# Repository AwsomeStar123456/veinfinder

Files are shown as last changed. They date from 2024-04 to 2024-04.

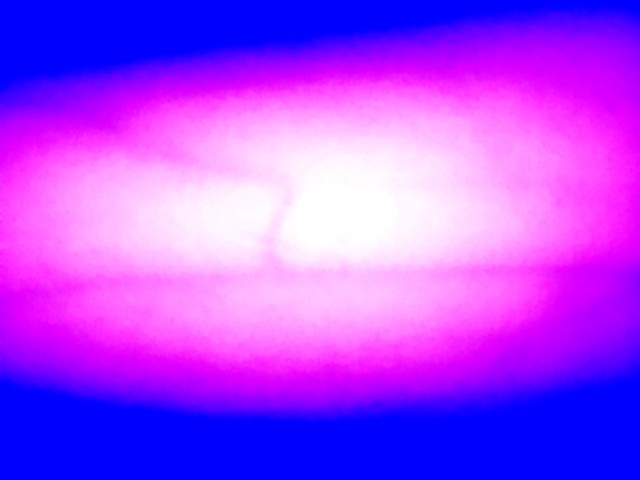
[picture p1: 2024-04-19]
Images/Original Image Set - Copy/Input/62.jpg

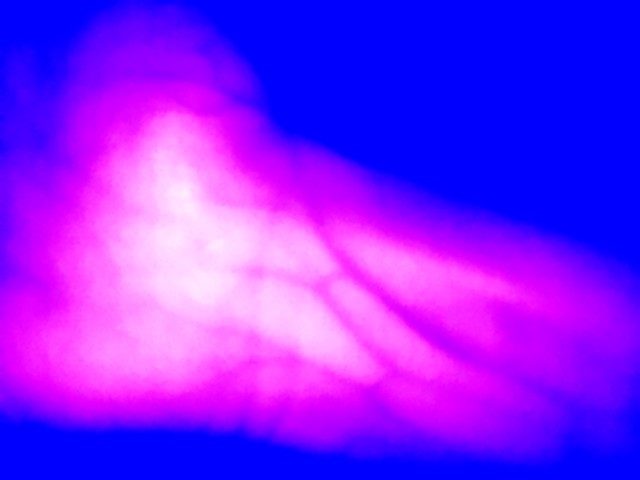
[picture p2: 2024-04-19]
Images/Original Image Set - Copy/Input/38.jpg

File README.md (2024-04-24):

# Veinfinder Project
This is the GitHub for the veinfinder project. Our project uses an IR emitter array with a NoIR Picam which has a IR pass filter on it. Using this we can see veins on peoples arms.

## Team Members
Donggi Lee | u1376432 | donggi2834@gmail.com <br />
Semrah Odobasic | u1293090 | semrahodobasic@icloud.com <br />
Logan Allen | u1190764 | Logan.Allen@utah.edu <br />
Jin Jeong   | u1375534 | djwls97865@gmail.com <br />

## Parts List
Raspberri Pi 2: https://www.raspberrypi.com/products/raspberry-pi-2-model-b/ <br />
NoIR PiCam 2: https://www.raspberrypi.com/products/pi-noir-camera-v2/ <br />
IR Emitter Array: https://www.ebay.com/itm/203067233072?chn=ps&norover=1&mkevt=1&mkrid=711-117182-37290-0&mkcid=2&mkscid=101&itemid=203067233072&targetid=2295557531990&device=c&mktype=pla&googleloc=9029771&poi=&campaignid=19851828444&mkgroupid=160536780385&rlsatarget=pla-2295557531990&abcId=9307249&merchantid=101644847&gad_source=1&gclid=Cj0KCQjwiYOxBhC5ARIsAIvdH51PvhkMOsm8p80wdNCZ_c5YhiLxNzNg80BskEwZZuzRu6qdxxyuCBwaApDhEALw_wcB <br />
Projector: https://www.amazon.com/KODAK-Luma-Pocket-Projector-Built/dp/B07RLXZ88F/ref=asc_df_B07RLXZ88F?tag=bngsmtphsnus-20&linkCode=df0&hvadid=80195746823025&hvnetw=s&hvqmt=e&hvbmt=be&hvdev=c&hvlocint=&hvlocphy=&hvtargid=pla-4583795273963725&psc=1 <br />
IR Pass Filter: https://www.amazon.com/dp/B0981BX423?psc=1&ref=ppx_yo2ov_dt_b_product_details <br />
Voltage Regulator: https://a.co/d/2TbWu2m <br />
Beam Splitter: https://www.amazon.com/dp/B00MA5S2YE?ref_=cm_sw_r_cso_cp_apin_dp_VDXDWMDAAD2QBHMKNW0C&starsLeft=1 <br />

## Files
### Documentation
The Documentation folder contains the documentation of our project. This includes all of the various documents that we created over the semester. Included is also a wiring diagram. The diagram shows how the power delivery works and how all of the components are connected to eachother. There is also an SOP which discusses how the veinfinder should be used.

### Images
This folder includes all of the training images we have taken along with the augmentation code. The augmentation code is in C# which we run using Visual Studio. There is a folder for the original image set of 117 images from 12 people. There is another folder which contains all of the augmented images. This folder contains 2,808 images which are augmented from the original dataset. We have found that this can give us a very good model.

### ML Models
This folder contains all of the models which we have deemed as successful. This contains the images showing how each epoch changes the model. There is also a text document where we outline the training set as well as the learning late. The actual models are too large to be uploaded to GitHub so they can be found here: https://drive.google.com/drive/folders/1DGls1SB5syulKGr5hgQqLpTfuY4aNmA4?usp=sharing

## Notes
The SOP contains a lot of valuable information. Please read it. Make sure you understand the wiring diagram.

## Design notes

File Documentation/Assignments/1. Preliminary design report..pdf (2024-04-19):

# Vein Finder Preliminary Design Report

이동기, 歐陽樂文, Semrah Odobašić, 정어진

Survey of the State-of-the-Art:

During our survey of existing products we noticed several things. First, vein finders already on the market for medical applications. Although, what we have found is that they are typically inaccessible to buy online without contacting these medical companies directly. As a result, their prices are also not publicly listed making it difficult to gauge cost [1]. We did find some options online from sites like Ebay however, which go for around $1,200. There are also other options such as the Veinlite which range in price from $250 - $550 which do not project back onto the arm [2].

Products like the AccuVein and our design use near-infrared (NIR) to detect veins. This system works due to our veins carrying deoxygenated blood with hemoglobin [3]. The hemoglobin absorbs the infrared which gives it a dark contrast compared to the tissue around the veins. Since this difference is very visible with our eyes it should be possible to use machine learning to identify the veins.

Our model that we currently have goes for around $270 compared to the $1,200 of the AccuVein or $250 (pediatric version) of the veinlite. The largest cost by far is the projector which is $179. Our hope is that we will eventually be able to find a more cost effective method of projecting the veins back to the arm.

[1] Vein Visualization System | AccuVein, Inc. (https://www.accuvein.com/vein-visualization-system/)
[2] Clinically Proven Vein Finders for IV Access (veinlite.com)
[3] Competitive Real-Time Near Infrared (NIR) Vein Finder Imaging Device to Improve Peripheral Subcutaneous Vein Selection in Venipuncture for Clinical Laboratory Testing - PMC (nih.gov) (https://www.ncbi.nlm.nih.gov/pmc/articles/PMC8067297/)

Imaging System:

For our preliminary system, we have a project previously worked on by another student at the University of Utah, Lance Delos Reyes. As part of his undergraduate research, he developed a system for vein finding to reduce cost over traditional systems used in the medical industry. As a result of his project, he managed to develop a system that could correctly image and display veins in the human body using near infrared LEDs, an infrared camera, and a simple projector. By shining the infrared LEDs on the skin, the hemoglobin in blood absorbs most of its light while the camera picks up everything that’s reflected back off the skin. Then using a raspberry pi 2 and some simple python scripts, the system processes the images by applying tone curves and using image segmentation to make the veins more visible. Finally, once the image is prepared, it’s displayed back on the skin to show the locations of the veins.

When we received the physical hardware from Lance, everything was already assembled and mostly working. When it came to imaging and displaying, the camera and projector worked, but it didn’t appear to be displaying or “finding” any veins. While it was difficult to tell exactly why the vein detection itself wasn’t working, we still have working electrical components, the raspberry pi, and his code repository itself so we could begin working on improvements in both hardware and software. In terms of other components included with the project, Lance was also using a 37Ah battery for power, and had the entire system secured in a 3D printed enclosure.

For our contributions to the project, we plan to update the design for the enclosure to make it more portable and robust. We also hope to improve the positioning of the LEDs and sensor in relation to the projector for more accurate placement of the image on the skin post processing. We hope that our solution will not only reduce noise produced by the projector, but also help with image focus and scaling depending on distance to the camera and projector. The rest of the improvements will then be done to the segmentation software, and we’ll likely explore the implementation of machine learning to better detect the veins for clearer images and more accurate results overall.

Parts List for Vein finder project:

1. Pi camera 2
- price : $23
- Purpose: captures images for vein detection.
- Quantity: 1
2. Raspberry pi 2 Model B
- Price: $39
- purpose : Serves as the central processing unit and machine learning unit for the vein finder.
- quantity : 1
3. IR Emitter
- Price: $3.06
- Purpose: Provides infrared illumination to enhance vein visibility.
- Quantity: 1
4. HDMI Ribbon cable (short)
- Price: $14.08
- purpose: connects the Raspberry pi board to mini projector for signal transmission. Here we used thin Ribbon type cable.
- Quantity: 1
●
5. DC-DC converter Module
- Price: $4 each
- Purpose: converts and regulates lithium-ion battery voltage to power components.
- quantity : 2
●
6. 3D print Materials
- Price: $3 per 200g
- Purpose: used for creating physical enclosure and mounting structures for the device
- quantity : As required

7. Projector
- Price: $179
- Purpose: projects image of the veins onto the skin for easy visualization
- Quantity: 1

Total: $269.14

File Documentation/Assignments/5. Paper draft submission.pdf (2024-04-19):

# NIR VeinFinder

Donggi Lee, Semrah Odobasic, Logan Allen, Jin Jeong

Abstract — Vein detection plays a crucial role in various medical procedures. It often becomes challenging for medical professionals to find options to help with veinfinding for patients with difficult to locate veins. This is because typical solutions can be expensive and large. We have created a vein finder which uses near infrared imaging with machine learning to find veins.

Keywords— U-Net, Infrared Imaging, Veinfinding, Segmentation.

I. A SURVEY OF THE STATE OF THE ART
During our survey of existing products we noticed several things. First, vein finders already exist on the market for medical applications. Although, what we have found is that they are typically inaccessible to buy online without contacting these medical companies directly. As a result, their prices are also not publicly listed making it difficult to gauge cost [1]. We did find some options online from sites like Ebay however, which go for around $1,200. There are also other options such as the Veinlite which range in price from $250 - $550 which do not project back onto the arm [2].

Products like the AccuVein and our design use near-infrared (NIR) to detect veins. This system works due to our veins carrying deoxygenated blood with hemoglobin [3]. The hemoglobin absorbs the infrared which gives it a dark contrast compared to the tissue around the veins. Since this difference is very visible with our eyes it should be possible to use machine learning and image alteration techniques to identify the veins.

Our current model goes for around $270 compared to the $1,200 of the AccuVein or $250 (pediatric version) of the veinlite. The largest cost by far is the projector which is $179. Our hope is that we will eventually be able to find a more cost effective method of projecting the veins back to the arm.

II. OUR PHYSICAL APPROACH
Our goal with this project is to create a vein finder that will show where your veins are. We do this by taking an IR image of your arm and then segment the veins using a U-Net machine learning model. This works well considering that veins carry hemoglobin which absorbs the IR light being used on your arm. Therefore, when NIR imaging is used, the veins come out well defined.

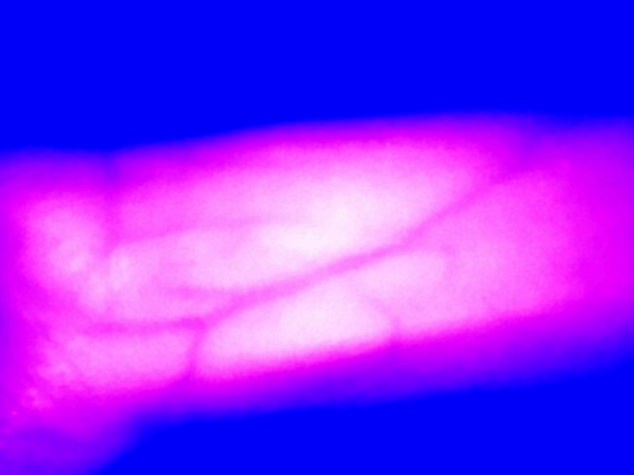
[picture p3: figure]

Fig. 1 An image from the camera of our vein finder showing well defined veins without the need of image processing..
Our setup involves a PiCam which is connected to a Raspberry Pi 2. The PiCam is in the middle of an IR emitting LED array. The PiCam is the NoIR version and we installed an IR pass filter onto it so that we could isolate the IR frequencies from visible light. The IR LEDs also use diffusers to spread out the IR for a clearer picture. We also have a projector which will be used in the future to project the veins back onto your arm.

All of this is enclosed in a custom 3D printed housing which is small and easy to carry. Using this setup we are able to capture very clear images which allows us to implement the machine learning portion much more efficiently.

III. OUR MACHINE LEARNING MODEL APPROACH
Given that the nature of our veinfinding project is to locate veins in people’s arms, the data collection process requires us to take pictures and work on data processing without a ground truth. This complicates our process of data collection as there is a manual segmentation step involved to pick the veins out of our images. Using these segmented images we can then train our UNet model. We started our data collection by taking a total of around 125 images of veins from 6 different people. From that we picked out the best images we had where you could see the veins clearly with the most contrast. That ended up giving us a total of 66 workable images which we then used to train our segmentation model. We ended up with a lot less photos than we initially took primarily because some veins were harder to find on certain people than others.

We then began to annotate our images for training the segmentation model. This was done by splitting the pictures we took between each team member and having each person individually highlight the veins in Photoshop. We drew over what we thought were veins with white then added a black background. This gives us the segmented veins while removing everything else. By the end, we then had 66 original images taken from our IR camera, and a matching annotation of the veins representing our ground truth that we could use to train a segmentation machine learning model.

The machine learning output from using our training set of 66 images was not usable so we decided to do data augmentation to increase the amount of training images we had. We did rotation, flipping, and various crops to create more images. This took us from our original set of 66 training images to 1,584. When we trained with this augmented dataset, the model worked much better producing very usable results.

We’re definitely happy at the moment with the images our camera can take and the segmentation our U-net model performs for segmentation. Our next steps however will be to start working on making the model outline more of the subtle veins in each of the images. If we have time we will also start to see if we can get the alignment of the projector set up so that we can display the vein images back onto the arm. From some basic tests, we determined that this becomes quite complex as the distance from the camera to the arm can vary.

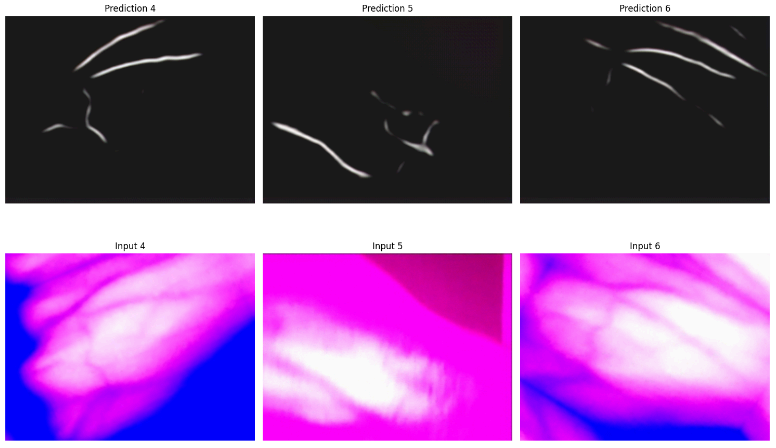
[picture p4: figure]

Fig. 2 Image showcasing the current segmentation ability of our model.

IV. CURRENT PROGRESS
Currently, we are more focused on training our model to give us better segmentation. We will do this by taking more images from additional users so that we can feed our model more varied data. Once we have an improved model we will connect it up to our program running on the Raspberry Pi. This will allow us to then feed live image data to the model so that we can segment in real time and use it to display the veins back on the user through the projector.
V. REFERENCES
[1] “Vein Visualization System,” AccuVein, Inc. https://www.accuvein.com/vein-visualization-system/
[2] “Clinically Proven Vein Finders for IV Access,” www.veinlite.com. https://www.veinlite.com/
[3] M. D. Francisco et al., “Competitive Real-Time Near Infrared (NIR) Vein Finder Imaging Device to Improve Peripheral Subcutaneous Vein Selection in Venipuncture for Clinical Laboratory Testing,” Micromachines, vol. 12, no. 4, p. 373, Mar. 2021, doi: https://doi.org/10.3390/mi12040373.

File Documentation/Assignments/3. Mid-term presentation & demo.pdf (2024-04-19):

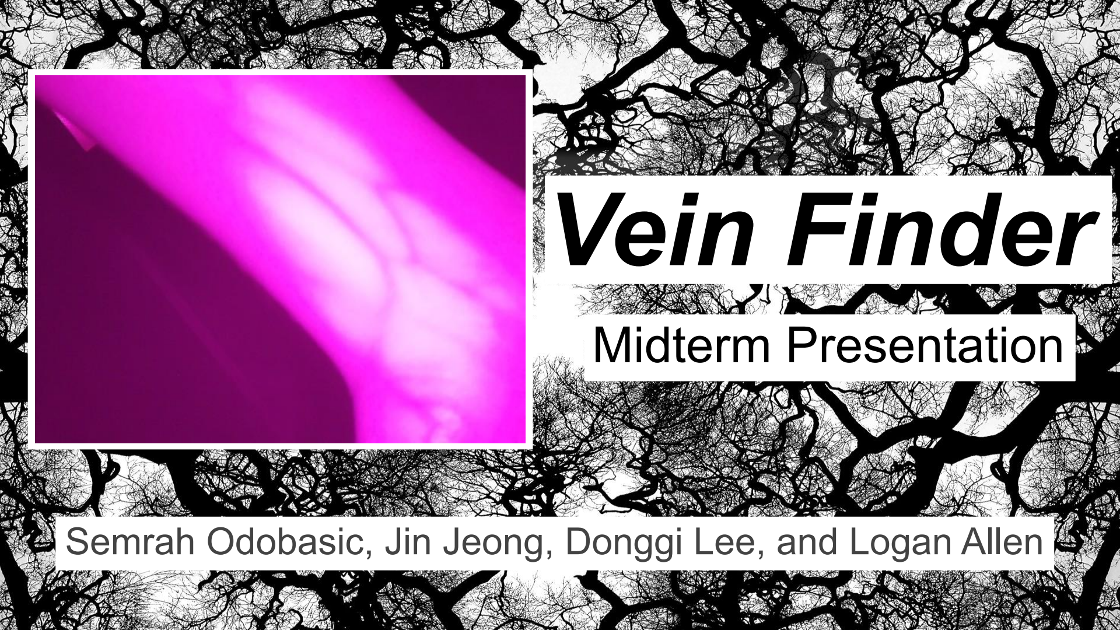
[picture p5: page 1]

Semrah Odobasic, Jin Jeong, Donggi Lee, and Logan Allen

## Midterm Presentation

# Vein Finder

## How does Veinfinder work?

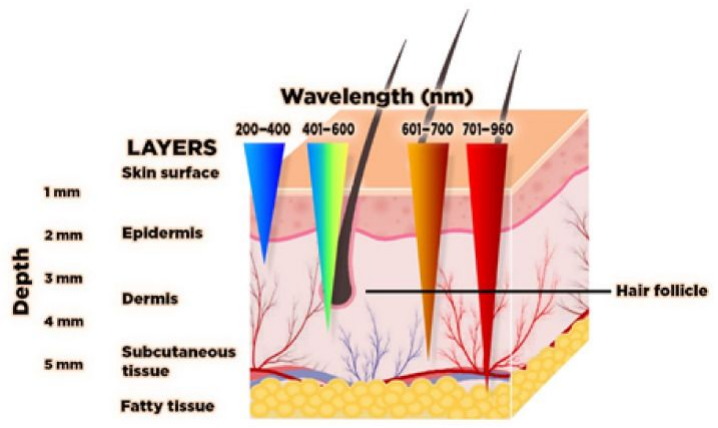
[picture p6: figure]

- Veins carry deoxygenated
blood with hemoglobin.
- Hemoglobin absorbs IR light which makes the veins visible in the IR spectrum.
- Our process includes shining IR light on to someone’s arm which will then then be visible using the Picam2 NoIR.

## Redesign of the Chassis

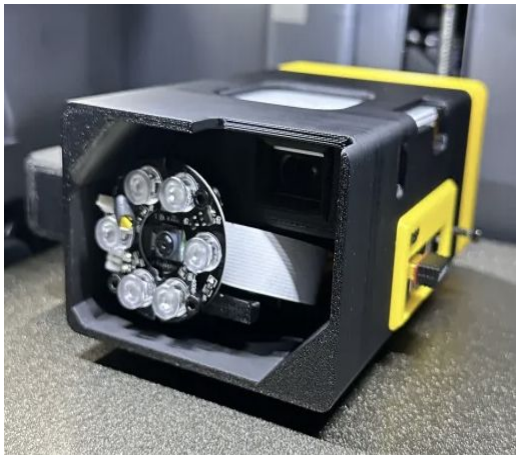
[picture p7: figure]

- Smaller Size
- More Robust and Reliable
- Easier to Debug
- Unibody Design
- Better Ergonomics
- Adjustable Camera Angle for Alignment using Ball Joint
- Removed 10000mAh Battery

## IR Pass Filter

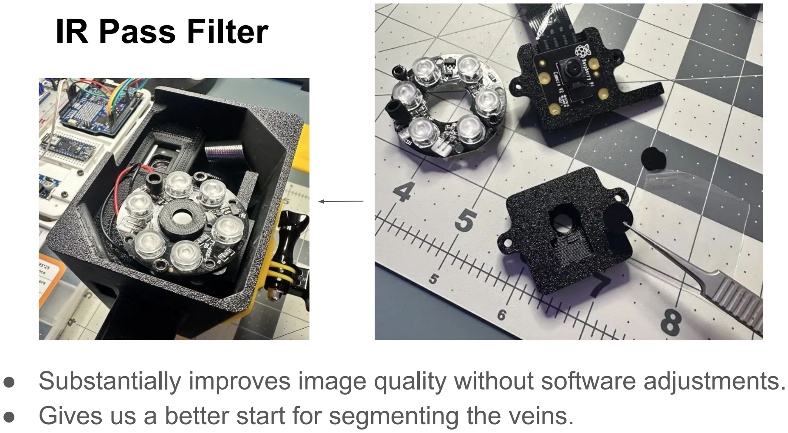
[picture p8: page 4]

- Substantially improves image quality without software adjustments.
- Gives us a better start for segmenting the veins.

## Data Collection for segmentation

- Took 10 different people’s veins, xxx workables
- Manual annotation of the Ground Truth (Veins)

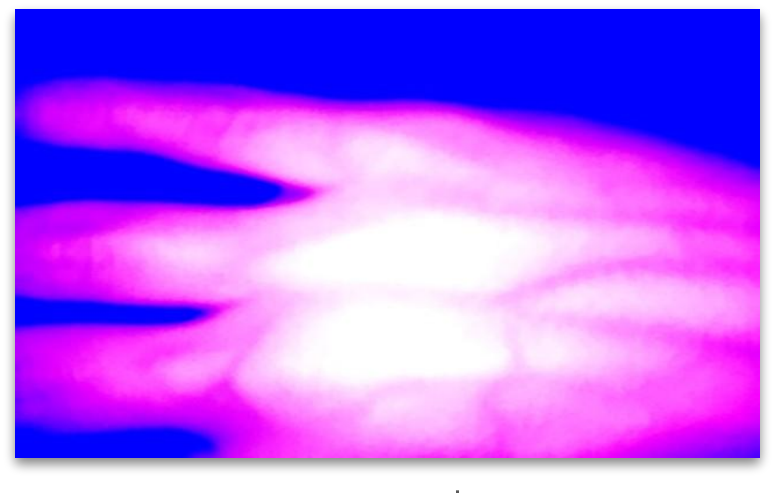
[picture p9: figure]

- Implemented the C# Script for Generating the Augmented Data

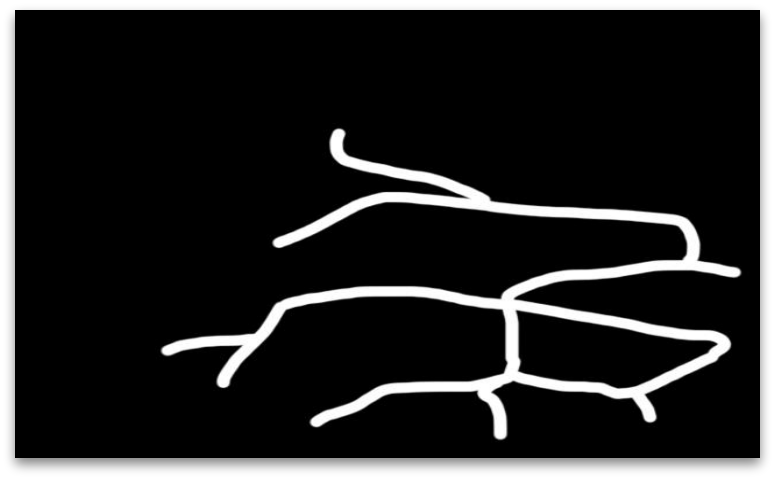
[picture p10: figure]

Data From 66 → xxxx

## Initial Model Training for Segmentation

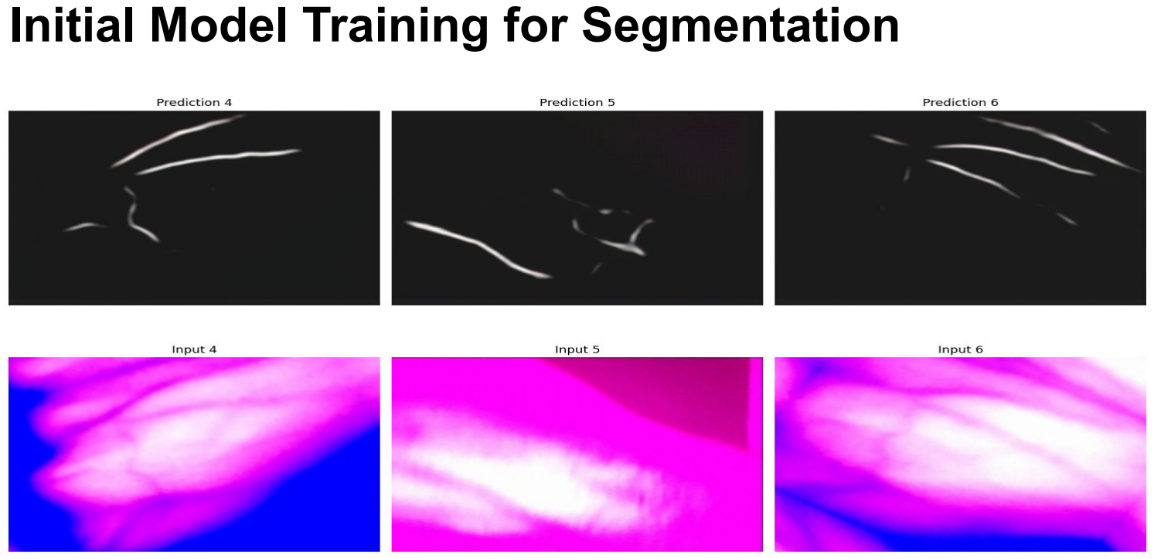
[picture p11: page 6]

## Improved Model Training for segmentation

// Add Picture for Improved model and the Output pictures, with same format aswell.

## Model Implementation

// Add the Picture for Live projecting the vein on the screen with the given Improved model

Semrah Odobasic, Jin Jeong, Donggi Lee, and Logan Allen

## Midterm Presentation

# Vein Finder

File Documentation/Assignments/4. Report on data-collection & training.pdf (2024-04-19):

# Vein Finder Data Collection & Training

이동기, 歐陽樂文, Semrah Odobašić, 정어진

# Data Collection

Given the nature of our veinfinding project to locate veins in people’s arms, the data collection process requires us to take pictures and work on data processing without a ground truth. This complicates our process of data collection as there will be a manual segmentation step involved to pick the veins out of our images for projecting back onto the user’s body. We started our data collection by taking a total of around 125 images of veins from 6 different people. From that we picked out the best images we had where you could see the veins clearly with the most contrast. That ended up giving us a total of 66 workable images which we then used to train our segmentation model. We ended up with a lot less photos than we initially took primarily because some veins were harder to find on certain people than others.

We then began to annotate our images for training the segmentation model. This was done by splitting the pictures we took between each team member and having each person essentially highlight the veins in Photoshop. This step is relatively trivial. We drew over what we thought were veins with white then added a black background. This gives us the segmented veins while removing everything else. By the end, we then had 66 original images taken from our IR camera, and a matching annotation of the veins representing our ground truth that we could use to train a segmentation machine learning model.

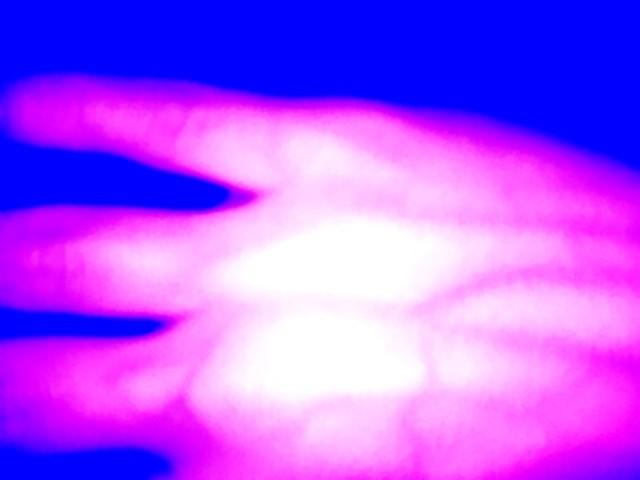
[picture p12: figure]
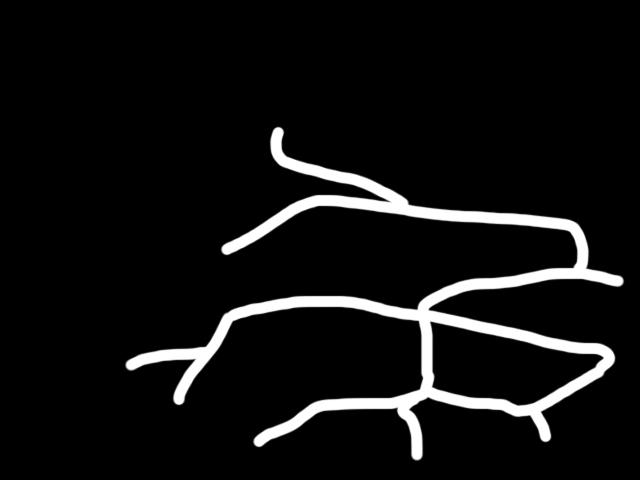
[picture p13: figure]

Fig 1: Original IR image (left) alongside the manual image annotations (right).

The segmentation model we used is a modified UNet provided by Rich Baird. We first tried to train the model using the original 66 images we took, but after trying different learning rates and number of epochs we found that the results were not good no matter what we tried. The determination was that this was due to not having a large enough sample size so we started work on augmentation so that we could rapidly expand our dataset.

# Data Augmentation

For data augmentation, the goal was to produce as many images as possible from the original 66 while still creating images that were useful. In order to keep the aspect ratio the same for all of our images, we unfortunately can’t do a rotation by 90 degrees since we’re using landscape photos. However, we were still able to perform other translations to get a new and much larger dataset. The initial augmentations that we applied was a 180° Rotation, Vertical Flip, and Horizontal Flip.

After the first set of augmentations we got a total of 264 images. From training our model on these images on top of our original 66, we did have much better results than before, but they were still not good enough for what we wanted. Seeing as this was the primary barrier for accurate training, we decided to augment these photos even further. For additional permutations, we chose to crop into different sections of our full size images and export back to 640x480 pixels. This was done by scaling the image by 125% and then cropping into the top left, top right, center, bottom left, and bottom right. This gave us another 1,320 images to work with for a total of 1,584.

For now, this is definitely a much better sample size to get results we are genuinely happy with. Due to the fact we can get magnitudes more images without having to take too many original photos means that the training process becomes much simpler and more accurate for our final result.

# Model Training

As we began training our UNet model, we logged the parameters we adjusted so we could determine which settings got us the best results. This would ensure that we could keep track of what was improving the quality and what was diminishing it. When we started training on the original dataset of 66 images the results were definitely not good. Usually it would result in weird coloring or a completely washed out gray image. This was consistent regardless of the learning rate or number of epochs we used.

After doing the first round of augmentations we tried to train again with a total of 264 images. This gave us predictions that were occasionally better and had slightly more definition on the veins, but other times we got the same results as before. We of course continued to tweak the epochs and learning rate to see what would happen and only got marginal improvements.

When we trained the model using the third set of augmentations with 1,320 photos however, the results were finally much better and more along the lines of what we were hoping to achieve. We finally ended up with correct coloring having a black background with the veins picked out in white. It also now properly identifies the veins with the only downside being that it prioritizes the largest ones. This is something we believe can definitely be improved on however by taking more images for the model to train with.

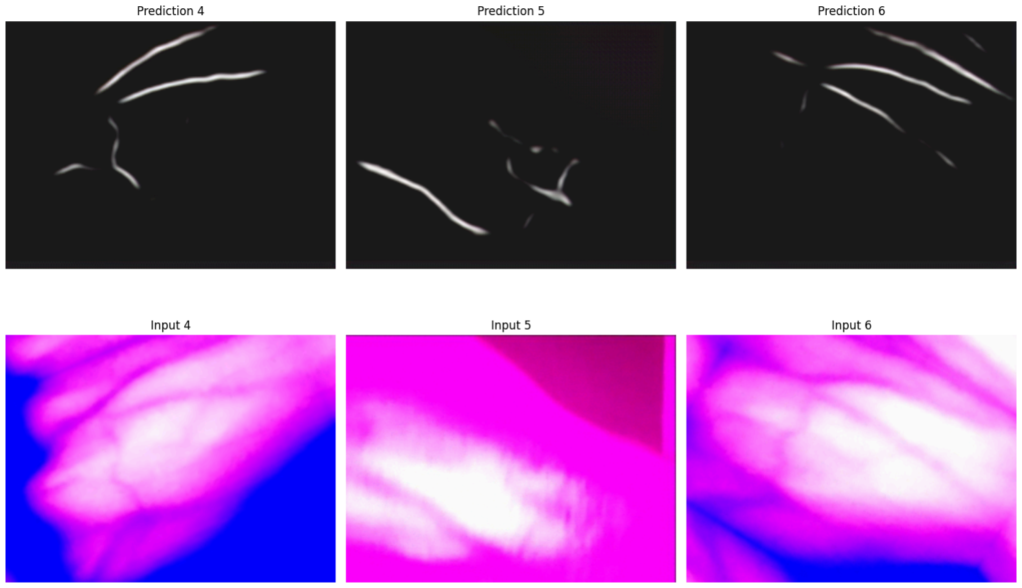
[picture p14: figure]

Fig 2: Image showcasing the current segmentation ability of our model.

Overall, we are very happy with the results we got from our final training run of the model but we believe that it can still be improved further. In addition to now fine tuning the learning rate and number of epochs for this dataset, we also hope to improve the quality of our input images to make the job easier on our model. Considering that we’re currently going from color to black and white images, we want to try pre-processing our images to grayscale so the model only has to focus on segmentation rather than color grading as well. We’ll also work on contrast and exposure adjustments so that as the images are being fed to our model, we’ll have the highest contrast images possible which will all be aimed at simplifying the segmentation task for the machine learning. Lastly, we’ll also continue to take more unique photos from new subjects so we can further diversify our dataset and provide even more data for the model to train on. Seeing as this has been the most effective at getting us to better results so far, we hope that this will provide the final push needed to have an effective vein finder by the completion of our project.

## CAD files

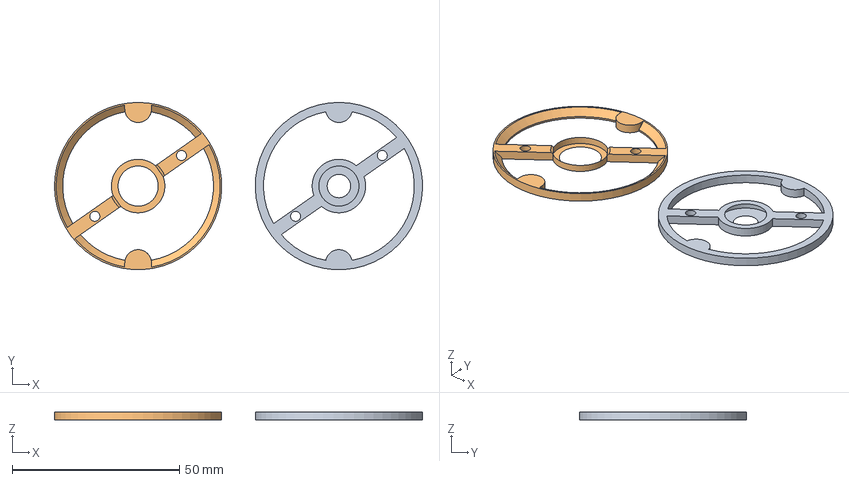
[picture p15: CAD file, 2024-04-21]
3D Print Files/vein finder diffuser holder v1.step
110.0 x 50.0 x 2.50 mm

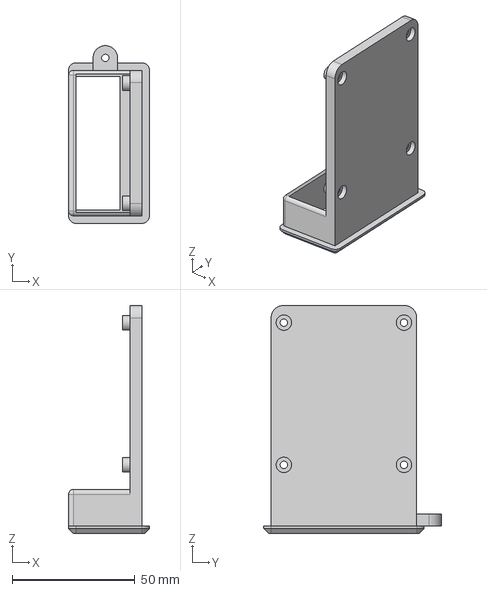
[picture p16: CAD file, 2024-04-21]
3D Print Files/veinfinder pi holder v5.step
33.0 x 72.5 x 93.0 mm

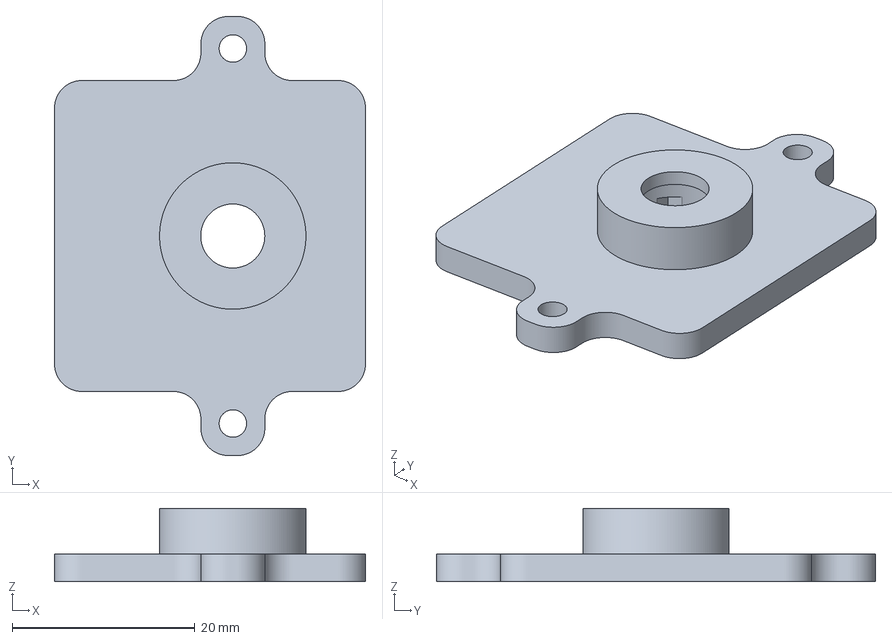
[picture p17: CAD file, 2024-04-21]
3D Print Files/Veinfinder Lens mount v1.3mf
34.0 x 48.0 x 8.00 mm

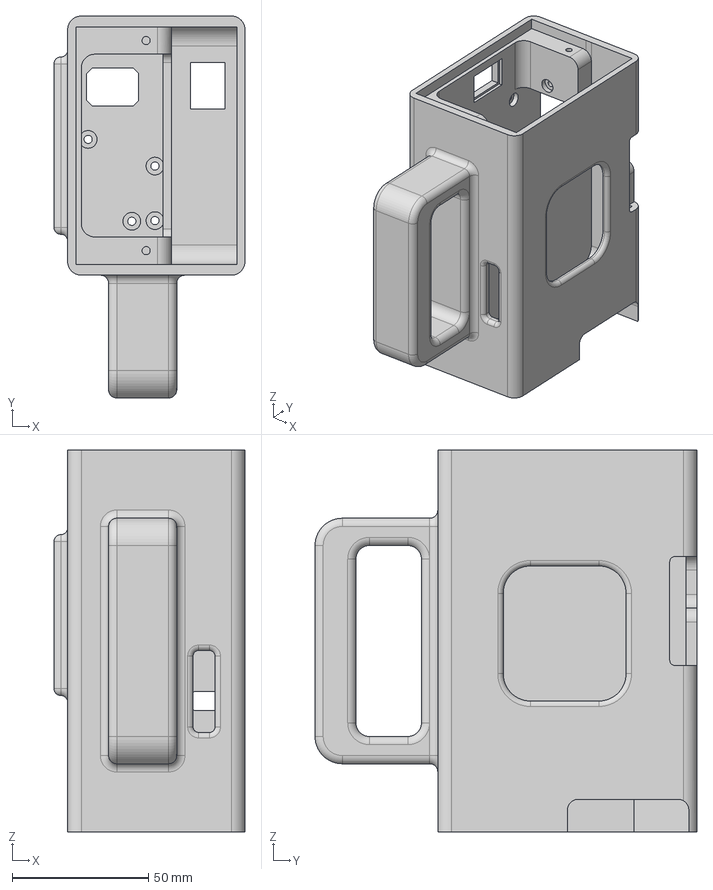
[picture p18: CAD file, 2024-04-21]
3D Print Files/veinfinder frame v9.step
70.0 x 140.0 x 140.0 mm

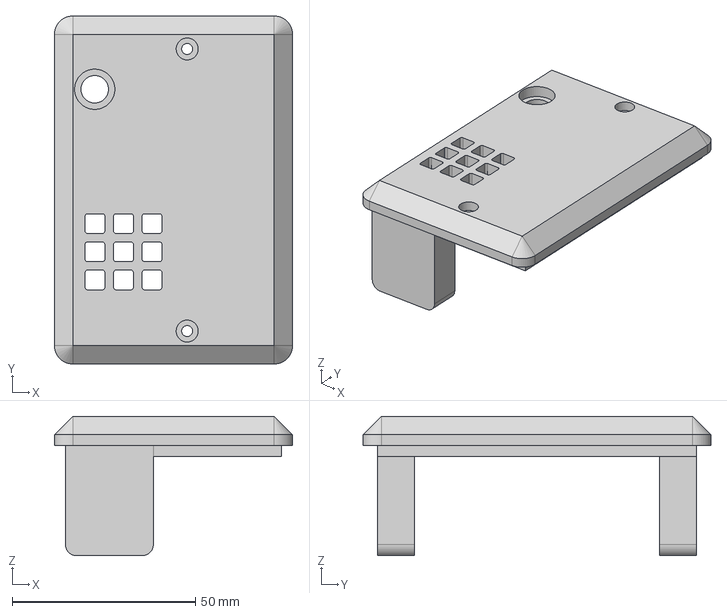
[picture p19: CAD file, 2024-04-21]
3D Print Files/Veinfinder back lid v6.step
65.0 x 95.0 x 38.0 mm

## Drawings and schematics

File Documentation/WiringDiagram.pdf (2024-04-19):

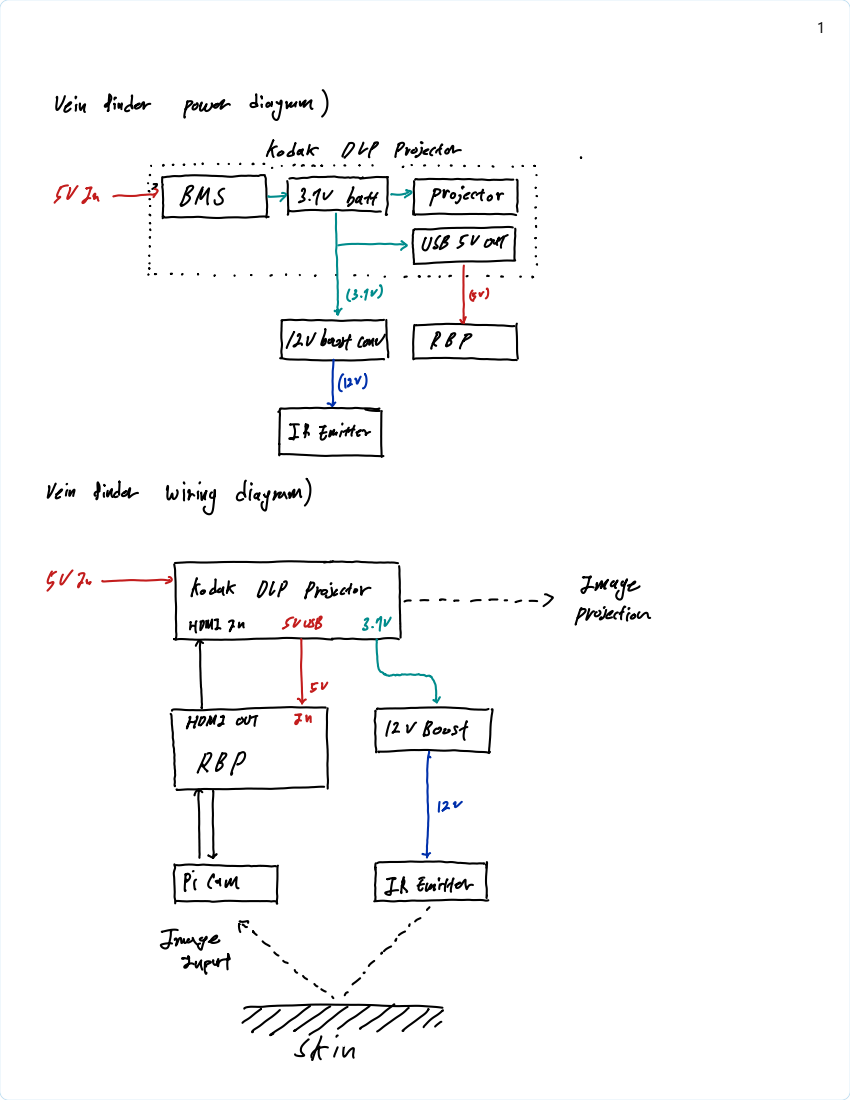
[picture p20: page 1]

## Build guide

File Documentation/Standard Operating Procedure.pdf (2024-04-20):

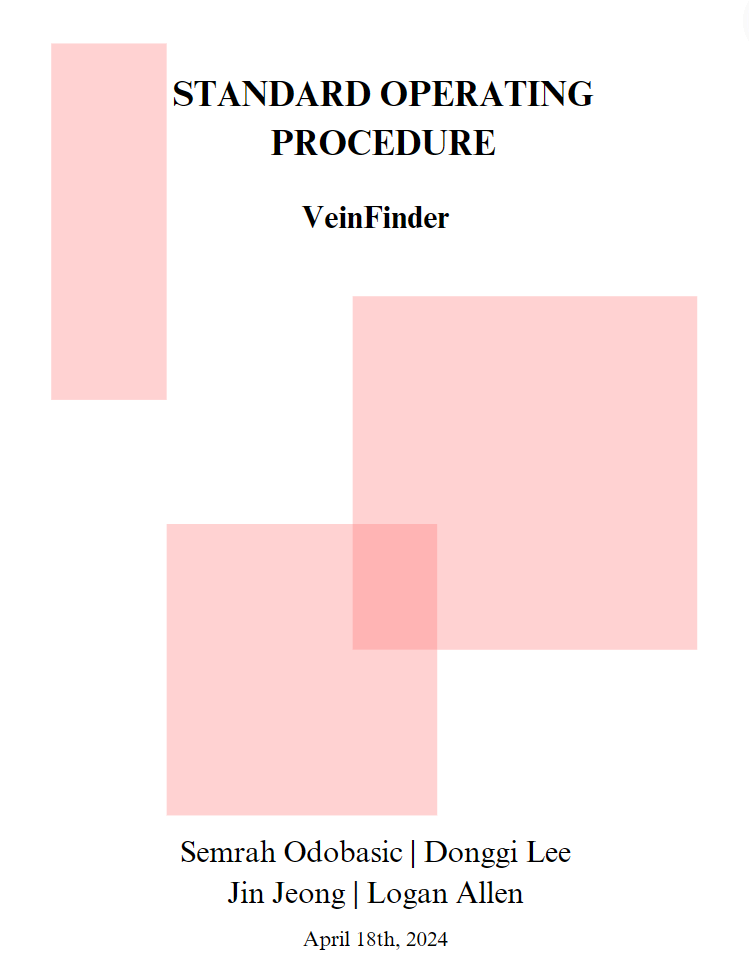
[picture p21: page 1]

### The Project

This project is a vein finder which assists people in finding veins using IR. Blood carries hemoglobin which absorbs IR light. When you apply IR light to the arm and take an image you can see the veins. We then want to take those images and segment them using a machine learning model. This is because the future goal is to use the onboard projector to project the veins back onto the arm. We will specifically use the U-Net designed by Rich Baird. This allows us to use lower quality hardware to get an image we can use.

### Hardware

Included
- Raspberry Pi 2
- NoIR PiCam 2
- IR Emitter Array
- Projector
- IR Pass Filter
- Voltage Regulator
- Custom 3D Printed Hardware

Required for Operation
- Keyboard
- Mouse
- Monitor
- HDMI Cable

### Software

Dependencies
- Picamera 2 Python Library
- OpenCV
- Numpy

The Software
The script “cameratesting.py” is the main file that you will use. It takes an image and outputs it on the screen. Overall it is very simple. It fixes the exposure, gain, contrast, auto white balance, and auto exposure to be fixed. They are currently set to the values that gave us the best results. There is also a file which has our first segmentation model. This model only uses OpenCV and doesn’t use any machine learning. It works to an extent but the machine learning segmentation model works better.

cameratesting.py & segmentation.py

### Operation

The operation of the camera is very simple. First, a keyboard and mouse should be connected to the raspberry pi. You also want to connect a monitor to the pi using an HDMI cable. Ideally you want to have a non IR reflective background so that the arm is clearly visible. You then want to turn on the projector. It powers everything from its internal battery so ensure that it is on. When the Pi powers up you want to run the “cameratesting.py” file which will run the script that uses the U-Net.

### Key Notes

The IR light has a switch on the bottom if you don't see any output check to make sure the switch is on. To confirm the IR is enabled you can open your camera app on your phone and look at the IR. It should look like it emits a purple light.

The vertical distance from the camera is important and varies from person to person. Move your hand up and down to ensure you get the best possible image.

Results vary. Some people can get great images while others struggle to get any veins to show up.

### Future Plan Recommendations

If anyone takes over this project we have a number of recommendations. First is that the Raspberry Pi should be upgraded to a newer model. This is because to do live segmentation using the U-Net model we need PyTorch. The PI 2 can only have a 32 bit OS so it cannot do it. Once you have a new PI on a 64 bit OS you can implement this part easily as it is documented in Rich’s code.

Once that is done we recommend doing the projection. The camera module can be rotated slightly which can help with making this work.

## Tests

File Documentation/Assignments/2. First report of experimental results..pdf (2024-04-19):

# Vein Finder First Report of Results

이동기, 歐陽樂文, Semrah Odobašić, 정어진

## State of the Art

During our survey of existing products we noticed several things. First, vein finders already exist on the market for medical applications. Although, what we have found is that they are typically inaccessible to buy online without contacting these medical companies directly. As a result, their prices are also not publicly listed making it difficult to gauge cost [1]. We did find some options online from sites like Ebay however, which go for around $1,200. There are also other options such as the Veinlite which range in price from $250 - $550 which do not project back onto the arm [2].

Products like the AccuVein and our design use near-infrared (NIR) to detect veins. This system works due to our veins carrying deoxygenated blood with hemoglobin [3]. The hemoglobin absorbs the infrared which gives it a dark contrast compared to the tissue around the veins. Since this difference is very visible with our eyes it should be possible to use machine learning and image alteration techniques to identify the veins.

Our model that we currently have goes for around $270 compared to the $1,200 of the AccuVein or $250 (pediatric version) of the veinlite. The largest cost by far is the projector which is $179. Our hope is that we will eventually be able to find a more cost effective method of projecting the veins back to the arm.

## Objective and Experiment Plans

- Project Objectives

- Lower cost.
- Simplify use.
- Reduce size.
- Improve hardware for obtaining better images in camera.
- Implement software to improve and alter images from the hardware.
- Project improved vein image back onto a patient’s arm.
- Experiments
- Test various IR emitters to improve hardware image quality.
- Test different lens filters to improve hardware image quality.
- Try various room conditions such as lights on and off.
- Implement various image alteration techniques to determine if the image can be further improved.
- See if there are any computer vision programs that can help segment the veins for display back onto the arm.
- Find methods to reduce the effect of the projector light on the received IR image in camera.

## Experimental Results to Date

Throughout these last few weeks we have made various changes and improvements to the vein finder. The first advancements we made were to improve the hardware. This was because the quality of the images being collected prior was low and already limited the amount of work the software could have done to improve the vein finding.

We first experimented with the vein finder we received from Lance to see how it worked and performed. During this process we identified that the IR emitters were being driven by a 5V source but noticed the silkscreen on the PCB for power said 12V. From using a phone camera on the IR emitter, we noticed only one of the IR LEDs was powered on at 5V so we determined that we needed to increase the voltage to the IR emitter. The voltages on the device were 3.3V and

5V from USB. Since this wasn’t what we needed, we used a voltage stepper to get 12V from the 3.7V USB supply. After looking at the images from the veinfinder again we immediately noticed all the LEDs powered on resulting in more IR light which slightly improved the images.

The images were still not great however so we decided to start improving other aspects of the hardware. One of the first things we had issues with was the portability and the fragility of the vein finder. In order to fix this we decided to remake the case and rewire the electrical systems. We first removed the breadboard and made a 3D printed case that has dedicated slots built in for all of the components. We then removed the original battery pack and used some smaller batteries instead. This will give us less run time but lowers the space required for the vein finder substantially.

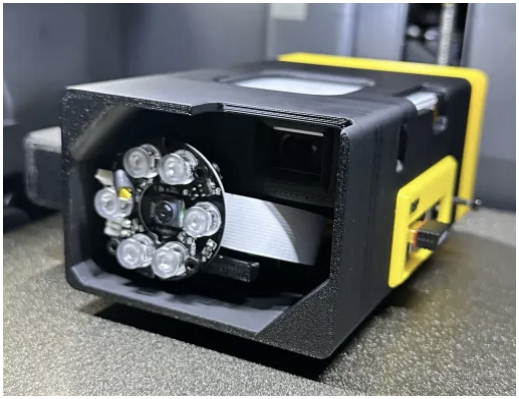
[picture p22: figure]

Fig 1: Image of the new vein finder case.

After improving the portability we then focused on getting a better image from in the camera. The first change we tried was using a different IR emitter that had more IR LEDs on it. When we used it with our camera however, we found that it did not improve the IR image we were receiving. After some discussion and research we found that the larger emitter produces IR at 950nm while the original emitter was producing IR at 800nm. After looking up the details for the Picam2 we found that there is a substantial drop in IR detection past 850nm which is why we didn’t see an improvement despite having more LEDs.

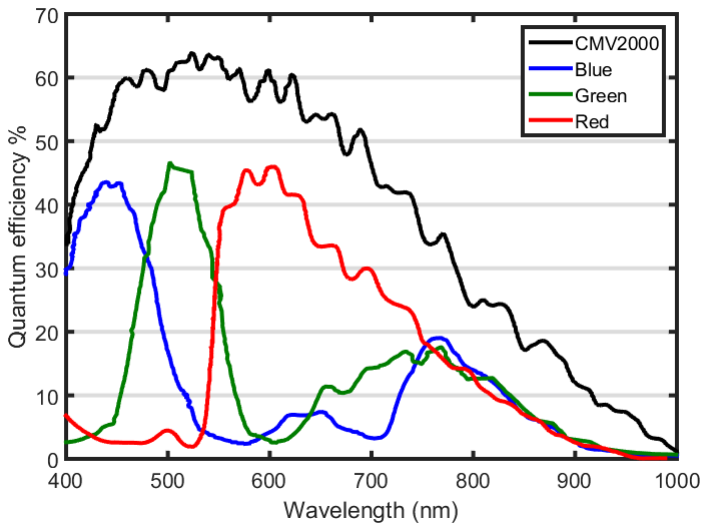
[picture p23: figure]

Fig 2: Wavelengths of the Sony IMX219.

From there, we chose to continue using the original emitter at 850nm. During our imaging tests however we found that visible light was also a slight complication. With the lights on in the room or the projector shining on an arm we found that we had too much visible light reflection to see anything in the NIR range. To fix that, we ordered an IR-Pass filter that allows light in wavelengths above 780nm.

While that was shipping we started looking at the software. The difficulty we had was with editing files since there was no PiOS desktop to go to. After attempting to get into the PiOS desktop from the SD card we had, we eventually gave up and started from scratch using our own image since we have the veinfinder code on Lance’s GitHub repository. During this process there were a number of dependencies we needed to install. The one we had the biggest issue with was OpenCV. After installing for about 3 hours it would crash with an error message. We read various forums on the internet and after about a week we managed to troubleshoot and get it working. We then installed the rest of the dependencies we needed and were able to get the program running from the PiOS desktop. With the help of Rich we were also able to download all of the existing files from the old SD card to our new environment.

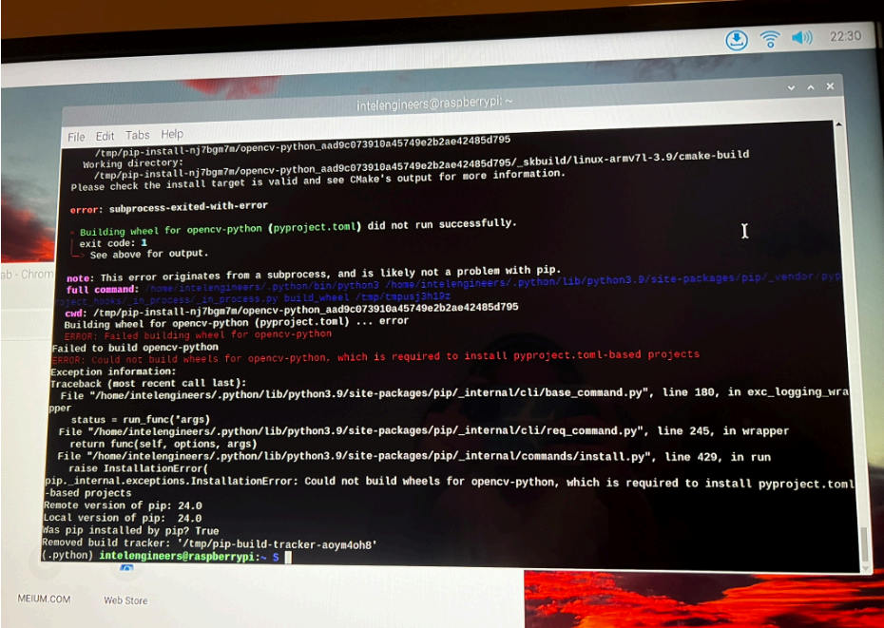
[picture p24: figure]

Fig 3: OpenCV error we were stuck on.

Once we had all of this we were able to make a simple program that just displays the image the camera is receiving. As before though the IR image quality was poor. We attempted to use tint for car windows from a recommendation online which did not work well in our case. Luckily, during this time the IR-pass filter eventually arrived so we could test that instead. After putting it over the lens we immediately had much better images coming directly from in camera with no software image processing or alterations. At this point, we are very happy with our progress as this now gives us a substantially better base image to begin altering in software.

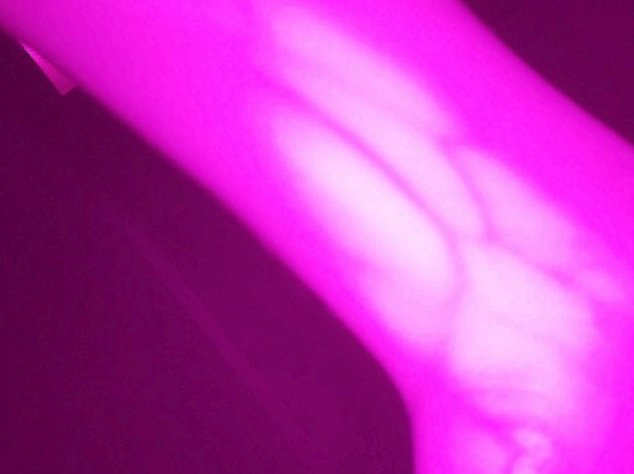
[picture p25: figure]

Fig 3: Initial results from implementing new hardware and the IR-Pass filter without software alterations.

## Semester Plans

- Current Objectives
- Develop an image processing algorithm to better highlight and accentuate veins from the camera’s filtered image.
- Take the image from the program and use the projector to display it back onto the arm.

- Implement a hardware system to be able to align the projector image in place on the arm.

## Credits

[1] Vein Visualization System | AccuVein, Inc. (https://www.accuvein.com/vein-visualization-system/)
[2] Clinically Proven Vein Finders for IV Access (veinlite.com)
[3] Competitive Real-Time Near Infrared (NIR) Vein Finder Imaging Device to Improve Peripheral Subcutaneous Vein Selection in Venipuncture for Clinical Laboratory Testing - PMC (nih.gov) (https://www.ncbi.nlm.nih.gov/pmc/articles/PMC8067297/)
